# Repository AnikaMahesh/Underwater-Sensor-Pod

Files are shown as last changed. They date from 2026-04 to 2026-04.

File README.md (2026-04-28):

# Underwater-Sensor-Pod

## Introduction
 This project aims to create a inexpensive servicable sensor pod. The sensor pod records underwater data such as temperature and depth data from lakes. It is serivible and can be open and closed to change batteries or change the sensors used. It stores data to a sd card which can be removed and inspected. Additionally if the sensor pod is out of water it should be able to send data over wifi. The current prototype records temperature data over time and stores it in a SD card and can be deployed underwater in a capsule.

## Summary of Files
`CAD files/caps.step` - File containing the end caps usedin the assembly.

`CAD files/pipe.step` - File for the Pipe used in the assembly

`CAD files/all thread rod.step` - File for the all thread rod used in the assembly

`CAD files/sensor pod.step` - File containing the assembled sensor pod.

`winch.ino` - Contains the code for the ESP32 that accesses the SD card, creates the file, gets the thermister output and converts it to celcius and Kelvin and updates the data file with these values every 500ms. 

## BOM
| Part | Quantity | Price(USD) | link |
|-------|-----|----------|------|
| SD card Module | 1 | $1.4  | https://www.amazon.com/dp/B07BJ2P6X6?ref=ppx_yo2ov_dt_b_fed_asin_title|
| Buck Boost Converter | 1 | $2 |https://www.amazon.com/dp/B0D8T3J8QZ?ref=ppx_yo2ov_dt_b_fed_asin_title |
| ESP32 Devkit | 1 | $4.5 |https://www.amazon.com/dp/B0DSZFD1SD?ref=ppx_yo2ov_dt_b_fed_asin_title&th=1 |
| Thermister | 1 | $2.5 |https://www.amazon.com/dp/B0FFZ9H843?psc=1&ref=ppx_pop_dt_b_product_details |
| AA Battery Holder | 1 | $0.8 |https://www.amazon.com/JWISLAND-Battery-Holder-Leads-Mount/dp/B0D1DPLZ77/ref=sr_1_1_sspa?dib=eyJ2IjoiMSJ9.wGKBVsK_WaEJNGbqqjIISVYdPiH7M6e4zWkNaY6G22fi9l_CXOmGQPM5VQd_All9ce3FouQ3wc62vfCCMd61VdhNM74E-bVmLZmcPDZ1odLfhOIwEuu04E8yfNUp_D2swvQ2hGOAF2QqiL3LkIHpraA4yh42gxxqIiqgS2xC6HaexNH40AiLFK8Vbk1N6ZEZdOEefdO0gCyQ_RRRXFxnN_k05GZN9WrCYsbp4x4aR48.XYwOc9-1n48rudYuBd_w9syITWB5iBJQvIOhxjMKF-k&dib_tag=se&keywords=AA%2Bbattery%2Bholder&qid=1777405177&sr=8-1-spons&sp_csd=d2lkZ2V0TmFtZT1zcF9hdGY&th=1|
| AA Battery | 2 | $1.56 |https://www.amazon.com/Duracell-Coppertop-AA-Ingredients-Long-lasting/dp/B0035LCFNQ/ref=sr_1_6?crid=1PJY5S4Z1IM14&dib=eyJ2IjoiMSJ9.kYYL580_QSYpdB85MGsyOOZVdFhchnkdNwyEs21cMNxHyO_zu1WGpOdmvtRh6o4NQMCmtpXKDADMnqElYNDfa7DAWeZUSeynO6oWFDg91ic5TL5UbLMg66W3VwieWh81fY0y1IIQT_6av0YZwtJItDjI9qPaRsOlAyGE02vtPJC8mq3-lsW3nYrLMV2fT2UFf_wt-FaIj7mEAsNGFeTW3pUUNFK-7tBw9m4jBewwkPn3-NeNcf9MXvHy6RPDQzi8MDWo0i2itzj0LOk-psceEGCLPV0JlE8-citnBHEzjjw.rFwUbdgsUlDZ5BEYBiEoIfdp-A4vC7H62tPbI3OKaag&dib_tag=se&keywords=AA+battery&qid=1777405257&rdc=1&sprefix=aa+battery+%2Caps%2C174&sr=8-6|
| Delrin Round | 3in | $26.58 |https://www.mcmaster.com/products/delrin-acetal-resin-rods/color~white/diameter~3-1-2/length~1-ft/|
| M5 Threaded Rods | 4 | $7.72 |https://www.amazon.com/dp/B0FMNTZFYR?ref=ppx_yo2ov_dt_b_fed_asin_title&th=1|
| M5 Hex Nuts | 8 | $0.56 |https://www.amazon.com/Kinhon-Rock-Stainless-Automotive-Industrial/dp/B0GJ37N9Y7/ref=sr_1_1_sspa?crid=2A11KZYJGQOXS&dib=eyJ2IjoiMSJ9.HvZn61SwVnhq1qOIBjcm4So77qIcb1yjq6-o3SHdhFdci99LuGTiGB5Lsk_9TJ8u52mo0sO-0Ar7_75YmM2UCmn41EjBG5-Ukeg9b_lbXPhbhgcXdiANE8xK230eRp4z3DY0V7mMu88_2hmPVcwzXVlcBDJG4DQCbzVNZw3B8oqoWVYFVVcFK0exYKFfLPOwE8XV6vdJ3pgRg-rwtaO0isTcuRwVVGMfm1UxaxRmZs2i6PGj0To_N1f5Oy93EwSKlFRWBncAegdp2B71AK6D3QDpmgpE_p2gzJWrYTGlTIE.o4hQ0mIbnBD7gg5nwaCy0oA3xVeKqTA6QP3DB5qsNp4&dib_tag=se&keywords=M5+hex+nuts&qid=1777405735&s=industrial&sprefix=m5+hex+nuts%2Cindustrial%2C210&sr=1-1-spons&sp_csd=d2lkZ2V0TmFtZT1zcF9hdGY&psc=1|
| PVC Pipe | 1 | $10 |https://www.amazon.com/MECCANIXITY-31-6mm-Impact-Aquarium-Greenhouse/dp/B0DP1X5ZFC/ref=sr_1_140_sspa?crid=2STKFL5ANB7NE&dib=eyJ2IjoiMSJ9.SRnaUdQA2jo3k_l1nlxflnqp647uhTZcyuxblo8_BV3aToQxuw-0TOXjpFUBNOgd9wsTtTyYCLe4LD0FI1xGOeL5ZhQJ6yBq_i9_MDTNdSRuRstn2U3iPcpvDBLNOAsKA8_xNmzlZLI9pnWIgCmFf74HKOm3HpMxciwSIg1VpjNE0Ofs6Gp3E7zHH4xe9JYLwGG0Yb2NromBAJL6zPbsARrZOdav5Pn19Ny6gQCcQOc80cxPDUPsROh60HuiCewZtsLzqMbzaASuzMFBq63CVkcxa7nDyFwfIjn2OlTCSNQ.cdc029Mz883X7-9OHRzYfl83dfzrnWWfcIoa2kqv47M&dib_tag=se&keywords=1.6%2Bin%2Bdiameter%2Bpvc%2Bpipe&qid=1777406587&s=hi&sprefix=1.6%2Bin%2Bdiameter%2Bpvc%2Bpip%2Ctools%2C96&sr=1-140-spons&xpid=wogcQ9SoyhVx-&sp_csd=d2lkZ2V0TmFtZT1zcF9idGY&th=1|
| SD card | 1 | $23.3 |https://www.amazon.com/dp/B0D5QPTFH9?psc=1&ref=ppx_pop_dt_b_asin_title|

 ## Enclosure
The sensor pod was designed to use a PVC pipe as a container. To seal the PVC pipe, 2 end caps were used. The end caps functioned as piston seals to ensure water does not get inside the enclosure and short out the electronics. The sensor pods would be held together by 4 M5 threaded rods and M5 hex nuts. This ensures that the caps stay on the PVC pipe. The CAD model is shown below.

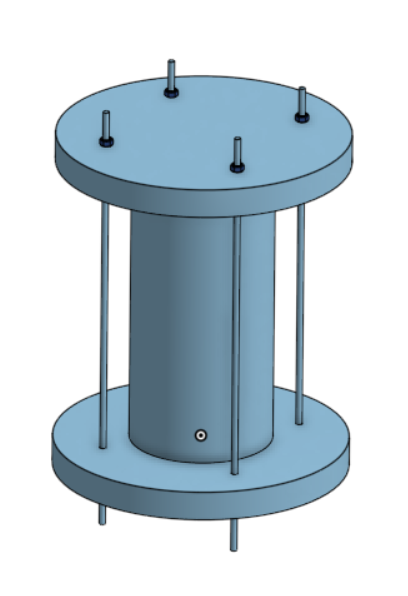
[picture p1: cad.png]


The O ring size used to seal the sensor pod were 3.40mm cross section diameter with 39.02 outer diameter because of this the slots were designed to have a slot of depth 2.71mm which creates a squeeze of 20% to properly seal the container. The following diagram was used to machine both the caps out of a cylinder of delrin. Delrin was chosen to make the sensor pod out of as it allows electromagnetic waves like radio waves to leave the sensor pod, enabling the components inside the sensor pod to communicate when not submerged in water. To ensure the O rings did not get cut when sliding the caps into the pipe, grease was applied and the edges of the pipes were champhered.

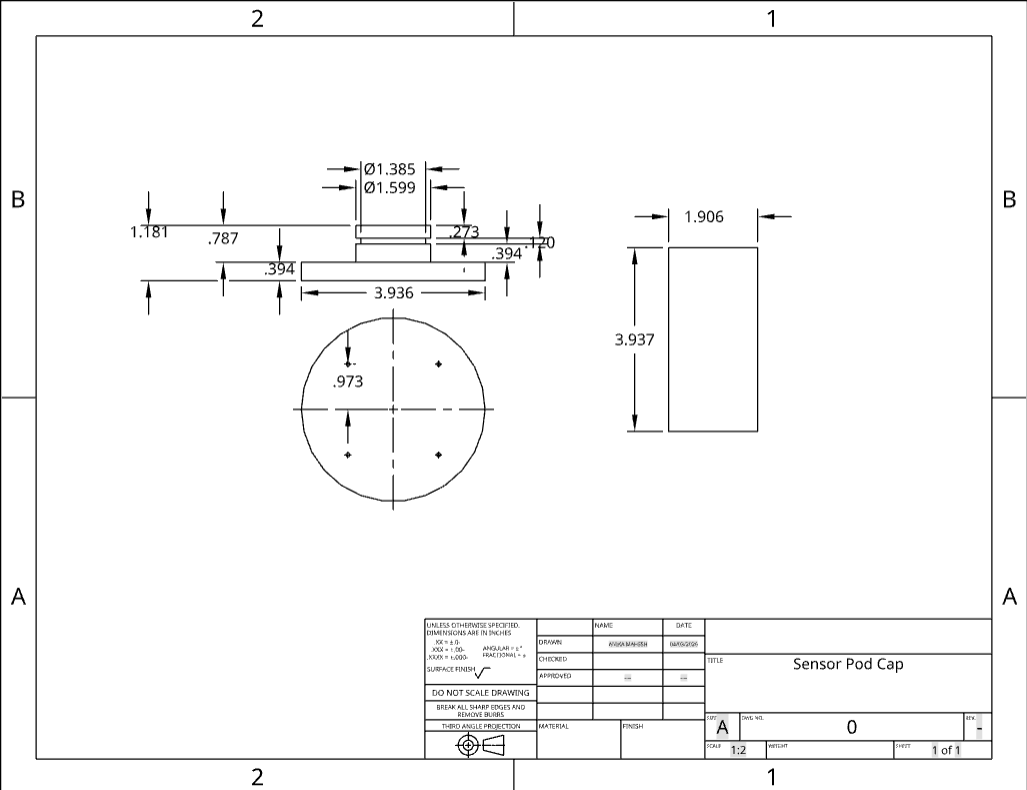
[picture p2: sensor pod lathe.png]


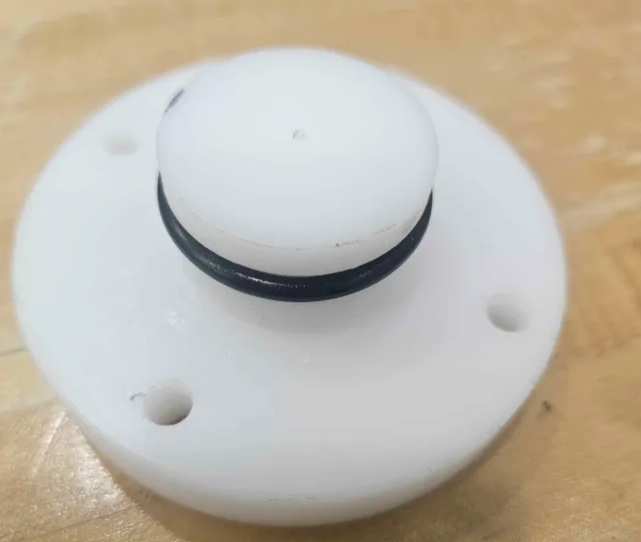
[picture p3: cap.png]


 ## Circuit
 For the SD card logging and the sensor recording the following circuit diagram was used. A esp32 was used as a microcontroller due to being inexpensive and very versatile, having analog and digital inputs and also being able to communicate wirelessly when not submerged in water.

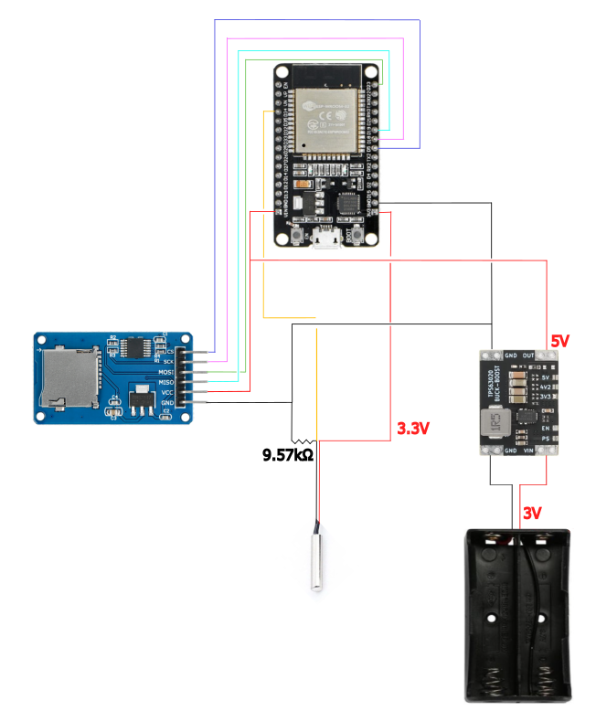
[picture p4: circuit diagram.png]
 

data is stored in a csv file recording the following values: 
Time(ms), Temperature(C), Temperature(analog value).

 ## Deployments

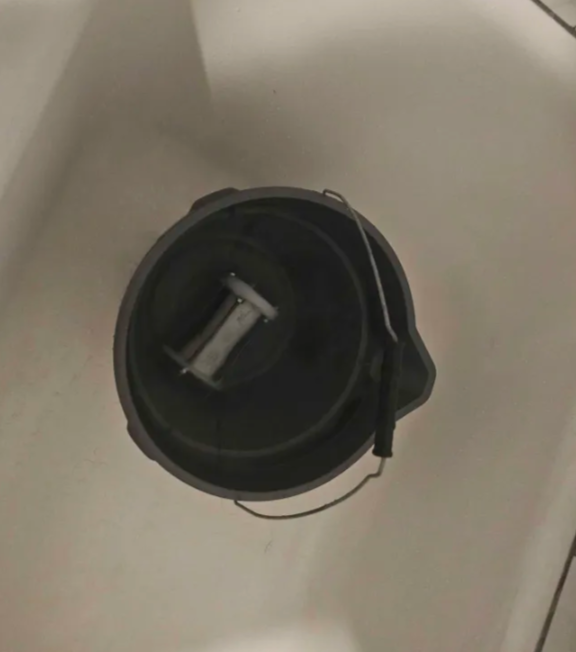
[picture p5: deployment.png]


The waterproofing was tested first by putting the sensor pod in water with a paper towel inside to see if they were any leaks. It was left inside a bucket for an hour and if it passed that deployment it would be put in water for 8 hours. The first time it was deployed for an hour one of the the caps was visibly leaking. This was because one of the threaded rods was slightly slanted. This was fixed by drilling another hole. After this it leaked less but after 8 hours the paper towel was not dry. After inspecting the caps I found that one of them had a deep groove in the slot. This was caused by stopping the lathe parting tool when it was in contact with the slot. So the lathe parting tool was used to shave off more material evenly to remove the grove. After this the sensor pod did not leak anymore however there was a bit of condensation on the paper tower which was remedied by a Desiccant Pack. The deployment was then successful.

 ## Future Work.
 Future work would be to replace the ESP32 with a STM 32 which would cause the sensor pod to be a lot more power efficient. Additionally more sensors would be incorporated. Currently the circuit is connected with point to point soldering however in the future this will be made more space efficient by ordering a PCB.

## Reflection
On entering this project i set the following goals for myself
- Learn to design housing and create CAD models.
- learn PCB design and ESP32 firmware coding.
- Learn and implement controls algorithms to do active heave compensation and snag detection

I did achieve some of these goals such as learning how to design underwater housings and create CAD models. I learned how to do waterproofing and calculate O ring slots. Additionally I did do ESP32 firmware coding and did learn about heave compensation and snag detection algorithms. However I did not design the PCB yet. Initially i was planning on designing a winch to deploy the sensor pod and wanted to do a bench test of the system. However in working on this project I made the decision to focus more on waterproofing the sensor pod and getting it to work in the bucket. While i didnt acheive all the learning goals, I did learn many things i wasnt initially intending to learn.

## Acknowledgements
Thanks to the Olin CREST lab and Prof. Victoria Preston for Advising on this project.

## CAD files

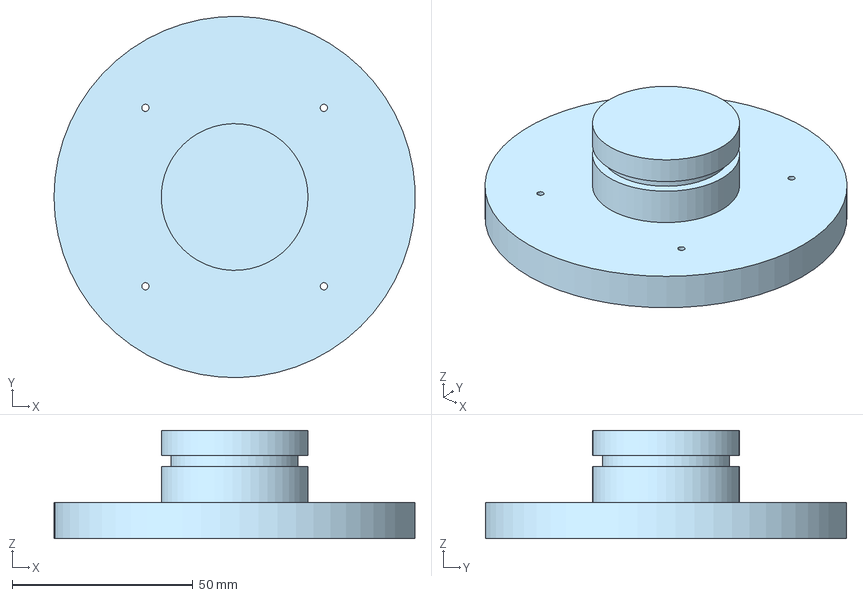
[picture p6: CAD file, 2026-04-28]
CAD files/caps.step
99.9 x 99.9 x 30.0 mm

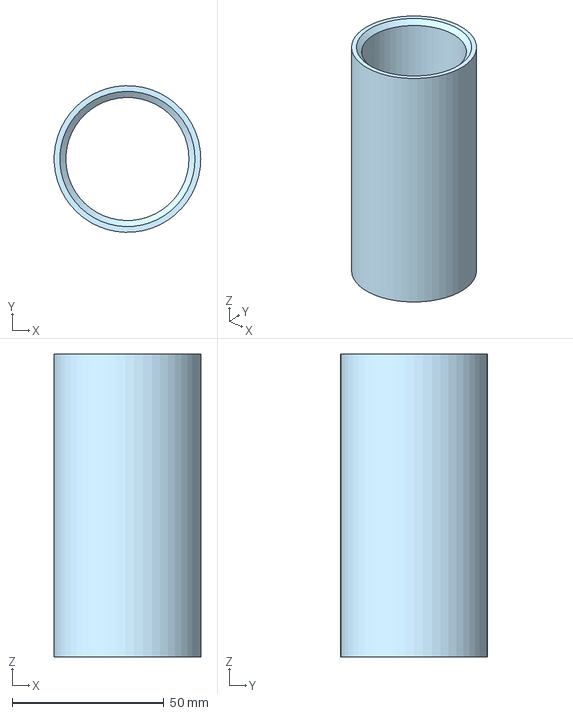
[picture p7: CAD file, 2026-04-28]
CAD files/pipe.step
48.4 x 48.4 x 100.0 mm

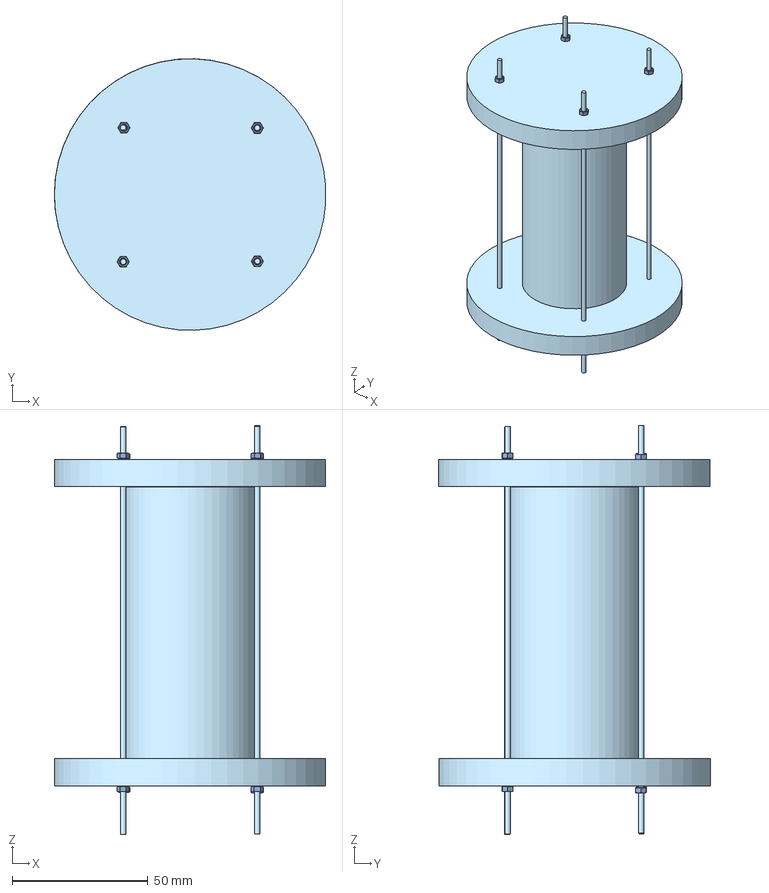
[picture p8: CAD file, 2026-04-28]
CAD files/sensor pod.step
99.9 x 100.0 x 150.6 mm
M5 Hex nut x 8

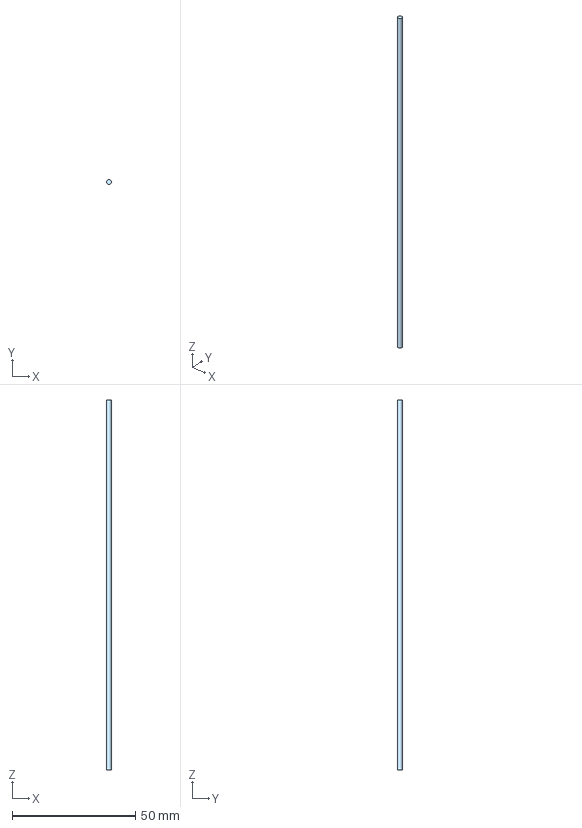
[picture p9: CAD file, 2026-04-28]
CAD files/all thread rod.step
1.99 x 1.99 x 150.0 mm

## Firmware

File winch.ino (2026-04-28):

#include "FS.h"
#include "SD.h"
#include "SPI.h"
const int analogPin = 34;
int thermval = 0;
float ms = 0;
void listDir(fs::FS &fs, const char * dirname, uint8_t levels){
  Serial.printf("Listing directory: %s\n", dirname);

  File root = fs.open(dirname);
  if(!root){
    Serial.println("Failed to open directory");
    return;
  }
  if(!root.isDirectory()){
    Serial.println("Not a directory");
    return;
  }

  File file = root.openNextFile();
  while(file){
    if(file.isDirectory()){
      Serial.print("  DIR : ");
      Serial.println(file.name());
      if(levels){
        listDir(fs, file.name(), levels -1);
      }
    } else {
      Serial.print("  FILE: ");
      Serial.print(file.name());
      Serial.print("  SIZE: ");
      Serial.println(file.size());
    }
    file = root.openNextFile();
  }
}

void createDir(fs::FS &fs, const char * path){
  Serial.printf("Creating Dir: %s\n", path);
  if(fs.mkdir(path)){
    Serial.println("Dir created");
  } else {
    Serial.println("mkdir failed");
  }
}

void removeDir(fs::FS &fs, const char * path){
  Serial.printf("Removing Dir: %s\n", path);
  if(fs.rmdir(path)){
    Serial.println("Dir removed");
  } else {
    Serial.println("rmdir failed");
  }
}

void readFile(fs::FS &fs, const char * path){
  Serial.printf("Reading file: %s\n", path);

  File file = fs.open(path);
  if(!file){
    Serial.println("Failed to open file for reading");
    return;
  }

  Serial.print("Read from file: ");
  while(file.available()){
    Serial.write(file.read());
  }
  file.close();
}

void writeFile(fs::FS &fs, const char * path, const char * message){
  Serial.printf("Writing file: %s\n", path);

  File file = fs.open(path, FILE_WRITE);
  if(!file){
    Serial.println("Failed to open file for writing");
    return;
  }
  if(file.print(message)){
    Serial.println("File written");
  } else {
    Serial.println("Write failed");
  }
  file.close();
}

void appendFile(fs::FS &fs, const char * path, const char * message){
  Serial.printf("Appending to file: %s\n", path);

  File file = fs.open(path, FILE_APPEND);
  if(!file){
    Serial.println("Failed to open file for appending");
    return;
  }
  if(file.print(message)){
      Serial.println("Message appended");
  } else {
    Serial.println("Append failed");
  }
  file.close();
}

void renameFile(fs::FS &fs, const char * path1, const char * path2){
  Serial.printf("Renaming file %s to %s\n", path1, path2);
  if (fs.rename(path1, path2)) {
    Serial.println("File renamed");
  } else {
    Serial.println("Rename failed");
  }
}

void deleteFile(fs::FS &fs, const char * path){
  Serial.printf("Deleting file: %s\n", path);
  if(fs.remove(path)){
    Serial.println("File deleted");
  } else {
    Serial.println("Delete failed");
  }
}

void testFileIO(fs::FS &fs, const char * path){
  File file = fs.open(path);
  static uint8_t buf[512];
  size_t len = 0;
  uint32_t start = millis();
  uint32_t end = start;
  if(file){
    len = file.size();
    size_t flen = len;
    start = millis();
    while(len){
      size_t toRead = len;
      if(toRead > 512){
        toRead = 512;
      }
      file.read(buf, toRead);
      len -= toRead;
    }
    end = millis() - start;
    Serial.printf("%u bytes read for %u ms\n", flen, end);
    file.close();
  } else {
    Serial.println("Failed to open file for reading");
  }


  file = fs.open(path, FILE_WRITE);
  if(!file){
    Serial.println("Failed to open file for writing");
    return;
  }

  size_t i;
  start = millis();
  for(i=0; i<2048; i++){
    file.write(buf, 512);
  }
  end = millis() - start;
  Serial.printf("%u bytes written for %u ms\n", 2048 * 512, end);
  file.close();
}

void setup(){
  Serial.begin(115200);
  delay(1000);
  Serial.println("started");
  if(!SD.begin(5)){
    Serial.println("Card Mount Failed");
    return;
  }
  pinMode(analogPin, INPUT);
  uint8_t cardType = SD.cardType();

  if(cardType == CARD_NONE){
    Serial.println("No SD card attached");
    return;
  }

  Serial.print("SD Card Type: ");
  if(cardType == CARD_MMC){
    Serial.println("MMC");
  } else if(cardType == CARD_SD){
    Serial.println("SDSC");
  } else if(cardType == CARD_SDHC){
    Serial.println("SDHC");
  } else {
    Serial.println("UNKNOWN");
  }

  uint64_t cardSize = SD.cardSize() / (1024 * 1024);
  Serial.printf("SD Card Size: %lluMB\n", cardSize);
  writeFile(SD, "/data.txt", "Time(ms), Temperature(C), Temperature (K), Temperature(analog value) \n");
  
  // listDir(SD, "/", 0);
  // createDir(SD, "/mydir");
  // listDir(SD, "/", 0);
  // removeDir(SD, "/mydir");
  // listDir(SD, "/", 2);
  // writeFile(SD, "/hello.txt", "Hello ");
  // appendFile(SD, "/hello.txt", "World!\n");
  // readFile(SD, "/hello.txt");
  // deleteFile(SD, "/foo.txt");
  // renameFile(SD, "/hello.txt", "/foo.txt");
  // readFile(SD, "/foo.txt");
  // testFileIO(SD, "/test.txt");
  // Serial.printf("Total space: %lluMB\n", SD.totalBytes() / (1024 * 1024));
  // Serial.printf("Used space: %lluMB\n", SD.usedBytes() / (1024 * 1024));
}

void loop(){
  float R_fixed = 9570.0;
  float R0 = 10000.0;
  float B = 3950.0;
  float T0 = 298.15;
  thermval = analogRead(analogPin);
  ms = millis();
  float V_ratio = thermval / 4095.0;
  float R_therm = R_fixed * (1.0 / V_ratio - 1.0);
  float tempK = 1.0 / ((1.0 / T0) + (1.0 / B) * log(R_therm / R0));
  float tempC = tempK - 273.15;
  String line = String(millis()) + "," +
                String(tempC, 3) + "," +
                String(tempK, 3) + "," +
                String(thermval) + "\n";

  appendFile(SD, "/data.txt", line.c_str());
  delay(100);
}
